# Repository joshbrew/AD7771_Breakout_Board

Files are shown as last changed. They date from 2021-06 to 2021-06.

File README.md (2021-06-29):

# AD7771_Breakout_Board
Unfinished AD7771 Breakout design. It works it's just not final.

The flex pieces were just unfinished thought experiments on a quick and dirty way to implement these AD7771 boards for FNIRS.

The board designs do work, but the Isolated DC-DC converter pin declarations in the schematics are backwards, found out the hard way so it is fixed in the design just not the footprint names in the .sch

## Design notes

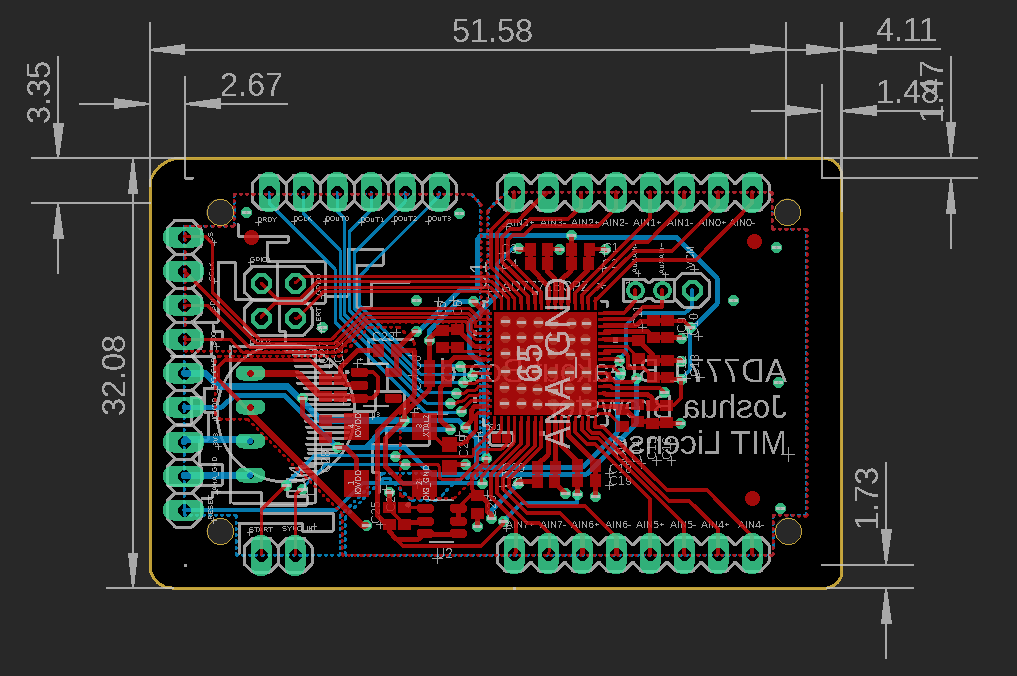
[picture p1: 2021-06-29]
AD7771.PNG

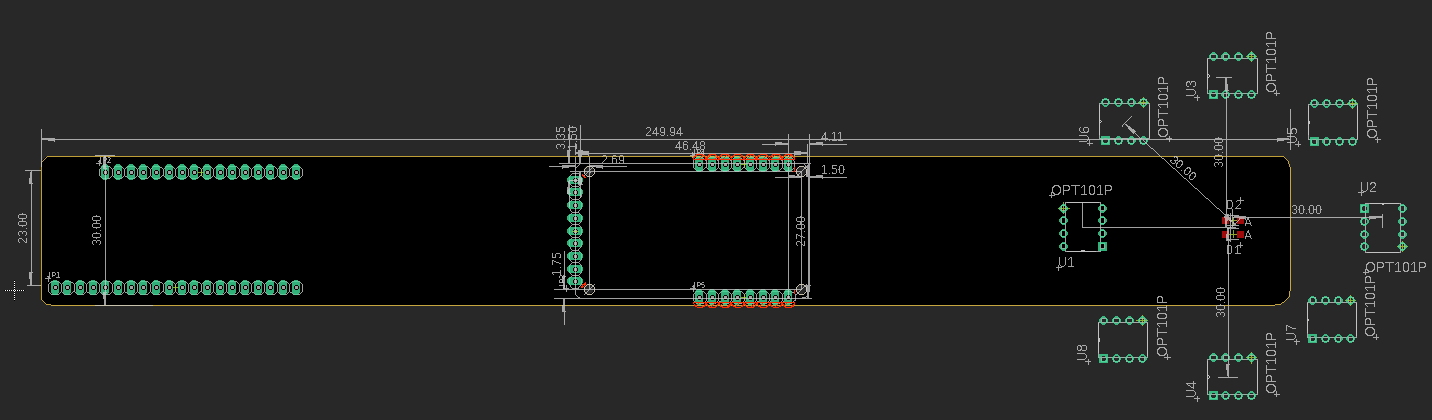
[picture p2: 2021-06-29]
FlexPiece_OCTO_Unfinished.PNG

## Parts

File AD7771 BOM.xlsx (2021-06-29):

Designation | Qty | Package | Value | Part # | Mouser Prices (high) | 1 | 10 | 100 | 1000 | Link
U1 | 1 |  |  | AD7771BCPZ | 584-AD7771BCPZ | 18.23 | 167.5 | 1345 | 11360 | https://www.mouser.com/ProductDetail/Analog-Devices/AD7771BCPZ
U2 | 1 |  |  | MAX6070AAUT25T | 700-MAX6070AAUT25+T | 2.63 | 23.6 | 183 | 1600 | https://www.mouser.com/ProductDetail/Maxim-Integrated/MAX6070AAUT25%2bT
U3 | 1 |  |  | LP5907MFX-3.3/NOPB | 595-LP5907MFX-3.3NPB | 0.55 | 4.31 | 32 | 191 | https://www.mouser.com/ProductDetail/Texas-Instruments/LP5907MFX-33-NOPB
U4 | 1 |  |  | TBA 1-0310 | 495-TBA1-0310 | 3.24 | 31.7 | 280 | 2430 | https://www.mouser.com/ProductDetail/TRACO-Power/TBA-1-0310
U5 | 1 |  |  | SG-210STF8.1920ML3 | 732-SG210STF8.1920L3 | 1.18 | 10.9 | 93.3 | 764 | https://www.mouser.com/ProductDetail/Epson-Timing/SG-210STF-81920ML3
C1, C3, C5, C8, C10, C13, C16, C19, C21, C22, C23 | 11 | C0402 | 1uF |  | 963-JMK105BJ105KP-F | 1.1 | 4.95 | 35.2 | 275 | https://www.mouser.com/ProductDetail/Taiyo-Yuden/JMK105BJ105KP-F?qs=vF%252B8ahGVilcfgxT2k6hjqQ%3D%3D
C2, C4, C6, C7, C9, C11, C12, C14, C15, C17, C18, C20, C24, C25, C26 | 14 | C0402 | 100nF |  | 963-LMF105B7104KVHF | 1.4 | 4.2 | 28 | 182 | https://www.mouser.com/ProductDetail/Taiyo-Yuden/LMF105B7104KVHF
C27 | 1 | C0402 | 10uF |  | 963-JMK105CBJ106MV-F | 0.22 | 1.02 | 8 | 51
 |  |  |  | via PCBway: | PCB Estimate (lead-free) | 18 | 18 | 50 | 235 | HASL lead free, 27mmX46.5mm, 2mm thick, any finish
 |  |  |  |  | Assembly Estimate | 88 | 88 | 232 | 520
 |  |  |  |  | Totals | 134.55 | 354.18 | 2286.5 | 17608
 |  |  |  | Additional Flex Piece Parts
 |  |  |  | OPT 101 |  | 0.9 | 9 | 90 | 900 | Aliexpress estimate
 |  |  |  | BR1102W |  | 0.5 | 3.09 | 14.2 | 119 | https://www.mouser.com/ProductDetail/Stanley-Electric/BR1102W-TR
 |  |  |  | HAN1102W |  | 0.38 | 2.5 | 16.1 | 126 | https://www.mouser.com/ProductDetail/Stanley-Electric/HAN1102W-1-TR
 |  |  |  | LOLIN32 |  | 4 | 40 | 400 | 4000 | Aliexpress estimate
 |  |  |  |  | Flex board by PCBway | 131 | 152 | 375 | 2336 | 250mmX30mm, 0.23mm thickness, 0.7mm thick FR4 stiffener (boths sides for manual assembly), ENIG
 |  |  |  |  | Extended Totals | 271.33 | 560.77 | 3181.8 | 25089
 |  |  |  | Other
 |  |  |  | Batteries | 300mAh-500mAh
 |  |  |  | Headband | Neoprene + plastic casing, something for the flex part.
 |  |  |  | Labor | Assembling the whole thing, testing, and packaging (done in-house)

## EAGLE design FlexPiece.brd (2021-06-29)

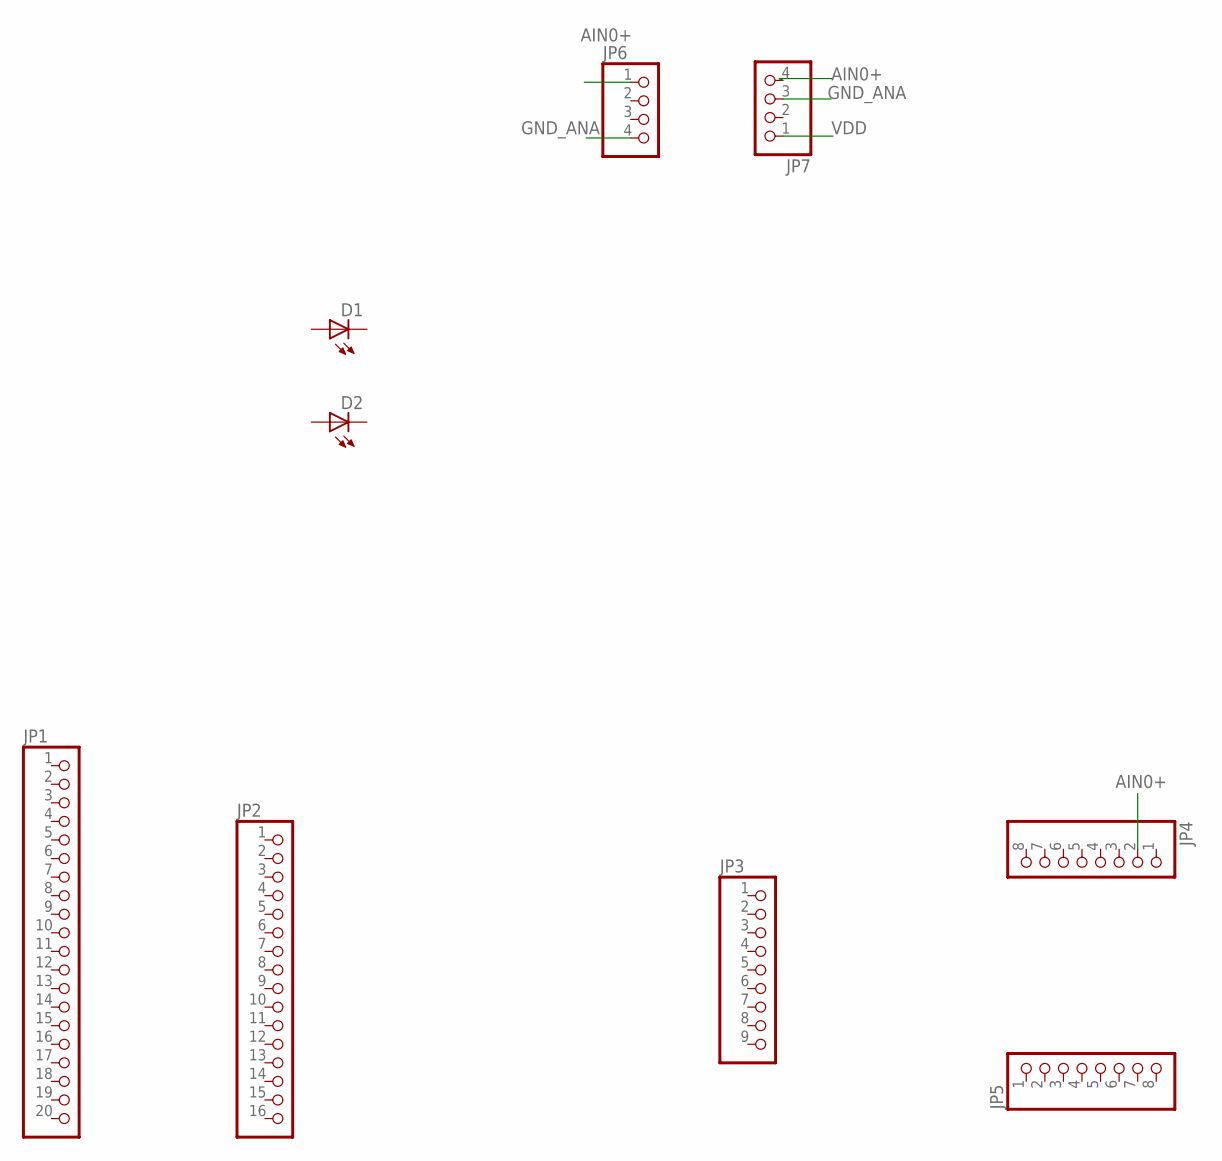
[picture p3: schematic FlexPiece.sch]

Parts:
D1, D2: LED1206; LED-1206
JP1: PINHD-1X20; 1X20
JP2: PINHD-1X16; 1X16
JP3: PINHD-1X9; 1X09
JP4, JP5: PINHD-1X8; 1X08
JP6, JP7: PINHD-1X4; 1X04

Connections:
AIN0+: JP4.2, JP6.1, JP7.4
GND_ANA: JP6.4, JP7.3
VDD: JP7.1

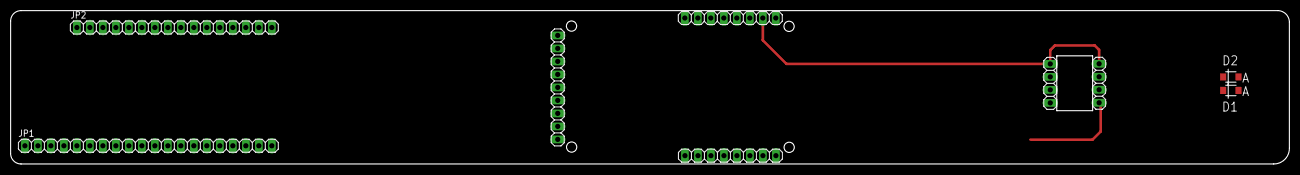
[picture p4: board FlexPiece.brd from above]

Board: 2 copper layers, 249.9 x 30.0 mm, 9 parts (0 on the bottom side), 2 nets.

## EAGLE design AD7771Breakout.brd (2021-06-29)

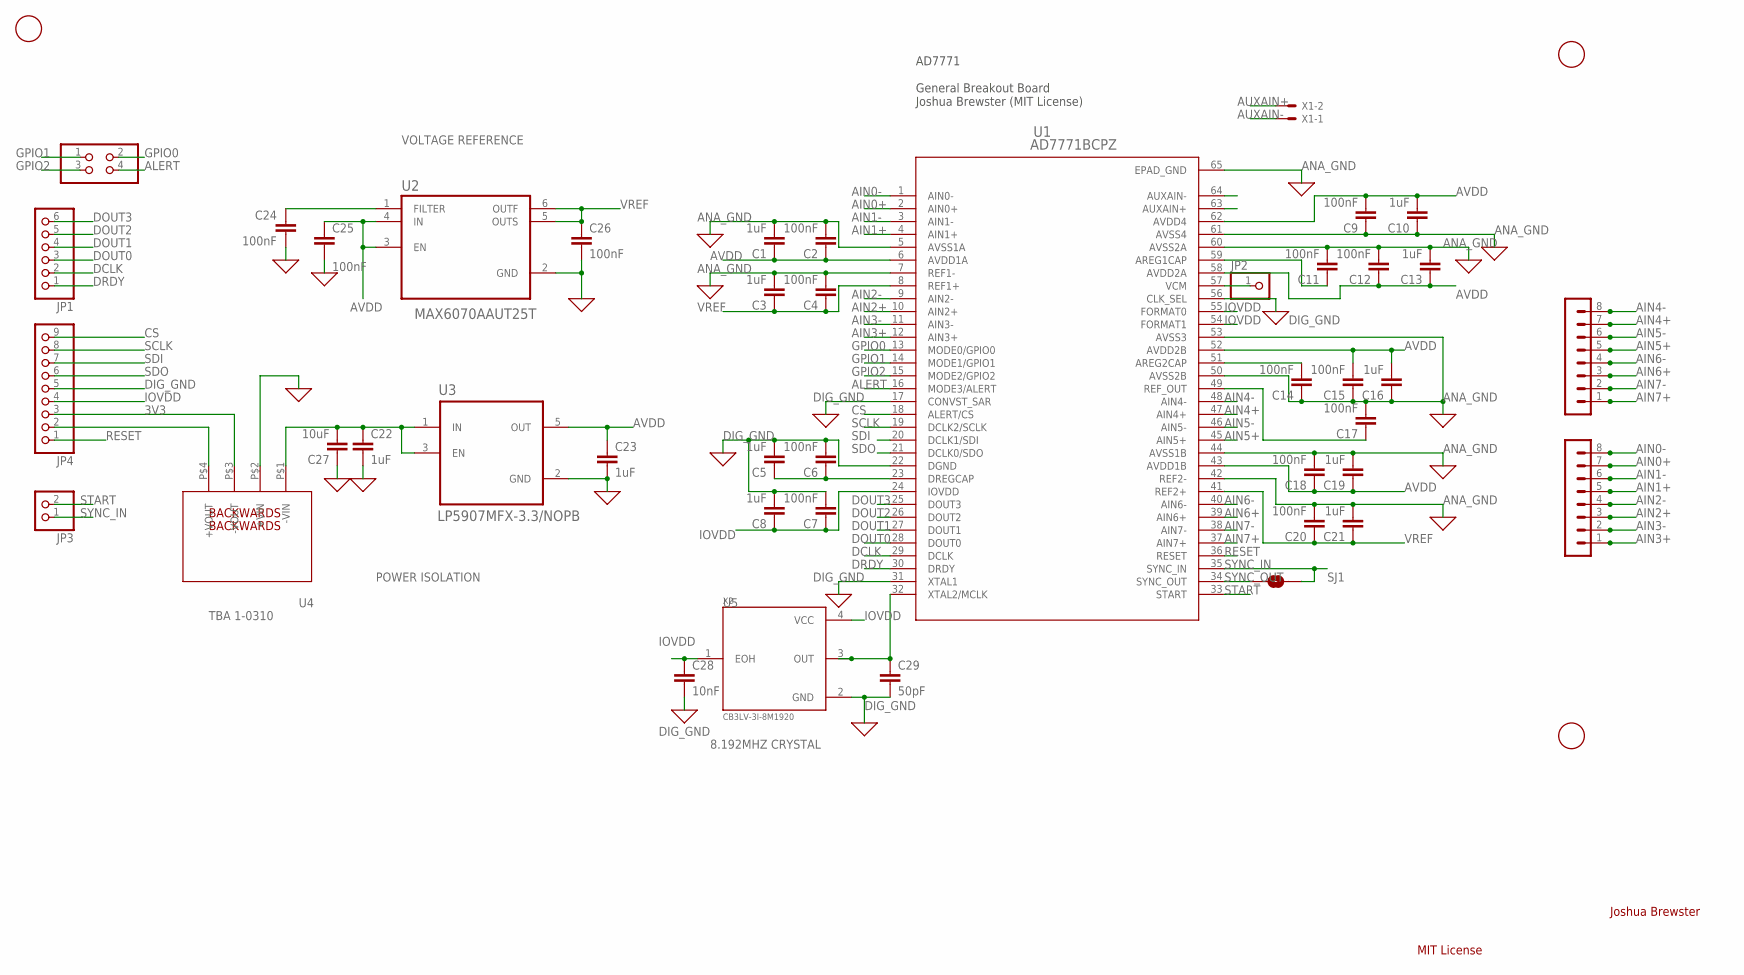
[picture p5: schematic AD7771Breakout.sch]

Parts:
C1, C3, C5, C8, C10, C13, C16, C19, C21, C22, C23: 1uF; C0402
C2, C4, C6, C7, C9, C11, C12, C14, C15, C17, C18, C20, C24, C25, C26: 100nF; C0402
C27: 10uF; C0402
C28: 10nF; C0402
C29: 50pF; C0603
JP1: PINHD-1X6; 1X06
JP2: PINHD-1X1; 1X01
JP3: PINHD-1X2; 1X02
JP4: PINHD-1X9; 1X09
JP5: PINHD-2X2; 2X02
SJ1: SOLDERJUMPERNC; SJ_2S_SMALL
SV4, SV5: MA08-1
U1: AD7771BCPZ; CP_64_15_ADI
U2: MAX6070AAUT25T; SOT95P280X145-6N
U3: LP5907MFX-3.3/NOPB; SOT95P280X145-5N
U4: TBA1-0310; SIP4-KT
U$1, U$2, U$5: FIDUCIAL; FIDUCIAL_1MM
X1: 332-02
X2: CB3LV-3I-8M1920; OSCCC700X500X180-4N

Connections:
3V3: JP4.3, U4.P$3 (-VOUT)
AGND_OUT: JP4.2, U4.P$4 (+VOUT)
AIN0+: SV4.7, U1.2 (AIN0+)
AIN0-: SV4.8, U1.1 (AIN0-)
AIN1+: SV4.5, U1.4 (AIN1+)
AIN1-: SV4.6, U1.3 (AIN1-)
AIN2+: SV4.3, U1.10 (AIN2+)
AIN2-: SV4.4, U1.9 (AIN2-)
AIN3+: SV4.1, U1.12 (AIN3+)
AIN3-: SV4.2, U1.11 (AIN3-)
AIN4+: SV5.7, U1.47 (AIN4+)
AIN4-: SV5.8, U1.48 (AIN4-)
AIN5+: SV5.5, U1.45 (AIN5+)
AIN5-: SV5.6, U1.46 (AIN5-)
AIN6+: SV5.3, U1.39 (AIN6+)
AIN6-: SV5.4, U1.40 (AIN6-)
AIN7+: SV5.1, U1.37 (AIN7+)
AIN7-: SV5.2, U1.38 (AIN7-)
ALERT: JP5.4, U1.16 (MODE3/ALERT)
ANA_GND: C1.2, C2.2, C3.2, C4.2, C9.1, C10.1, C11.2, C12.2, C13.2, C14.1, C15.1, C16.1, C17.2, C18.2, C19.2, C20.2, C21.2, C22.2, C23.2, C24.2, C25.2, C26.2, C27.1, U1.5 (AVSS1A), U1.7 (REF1-), U1.42 (REF2-), U1.44 (AVSS1B), U1.50 (AVSS2B), U1.53 (AVSS3), U1.60 (AVSS2A), U1.61 (AVSS4), U1.65 (EPAD_GND), U2.2 (GND), U3.2 (GND), U4.P$2 (+VIN)
AREG1CAP: C11.1, U1.59 (AREG1CAP)
AREG2CAP: C14.2, U1.51 (AREG2CAP)
AUXAIN+: U1.63 (AUXAIN+), X1.2
AUXAIN-: U1.64 (AUXAIN-), X1.1
AVDD: C1.1, C2.1, C9.2, C10.2, C12.1, C13.1, C15.2, C16.2, C18.1, C19.1, C23.1, C25.1, U1.6 (AVDD1A), U1.43 (AVDD1B), U1.52 (AVDD2B), U1.58 (AVDD2A), U1.62 (AVDD4), U2.3 (EN), U2.4 (IN), U3.5 (OUT)
CS: JP4.9, U1.18 (ALERT/CS)
DCLK: JP1.2, U1.29 (DCLK)
DIG_GND: C5.2, C6.2, C7.2, C8.2, C28.2, C29.2, JP4.5, U1.17 (CONVST_SAR), U1.22 (DGND), U1.31 (XTAL1), U1.56 (CLK_SEL), X2.2 (GND)
DOUT0: JP1.3, U1.28 (DOUT0)
DOUT1: JP1.4, U1.27 (DOUT1)
DOUT2: JP1.5, U1.26 (DOUT2)
DOUT3: JP1.6, U1.25 (DOUT3)
DRDY: JP1.1, U1.30 (DRDY)
DREGCAP: C5.1, C6.1, U1.23 (DREGCAP)
FILTER: C24.1, U2.1 (FILTER)
GPIO0: JP5.2, U1.13 (MODE0/GPIO0)
GPIO1: JP5.1, U1.14 (MODE1/GPIO1)
GPIO2: JP5.3, U1.15 (MODE2/GPIO2)
IOVDD: C7.1, C8.1, C28.1, JP4.4, U1.24 (IOVDD), U1.54 (FORMAT1), U1.55 (FORMAT0), X2.1 (EOH), X2.4 (VCC)
REF_OUT: C17.1, U1.49 (REF_OUT)
RESET: JP4.1, U1.36 (RESET)
SCLK: JP4.8, U1.19 (DCLK2/SCLK)
SDI: JP4.7, U1.20 (DCLK1/SDI)
SDO: JP4.6, U1.21 (DCLK0/SDO)
START: JP3.2, U1.33 (START)
SYNC_IN: JP3.1, SJ1.2, U1.35 (SYNC_IN)
SYNC_OUT: SJ1.1, U1.34 (SYNC_OUT)
VCM: JP2.1, U1.57 (VCM)
VOUT+: C22.1, C27.2, U3.1 (IN), U3.3 (EN), U4.P$1 (-VIN)
VREF: C3.1, C4.1, C20.1, C21.1, C26.1, U1.8 (REF1+), U1.41 (REF2+), U2.5 (OUTS), U2.6 (OUTF)
XTAL2: C29.1, U1.32 (XTAL2/MCLK), X2.3 (OUT)

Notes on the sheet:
AD7771 General Breakout Board Joshua Brewster (MIT License)
TBA 1-0310
POWER ISOLATION
VOLTAGE REFERENCE
8.192MHZ CRYSTAL
Joshua Brewster
MIT License
BACKWARDS

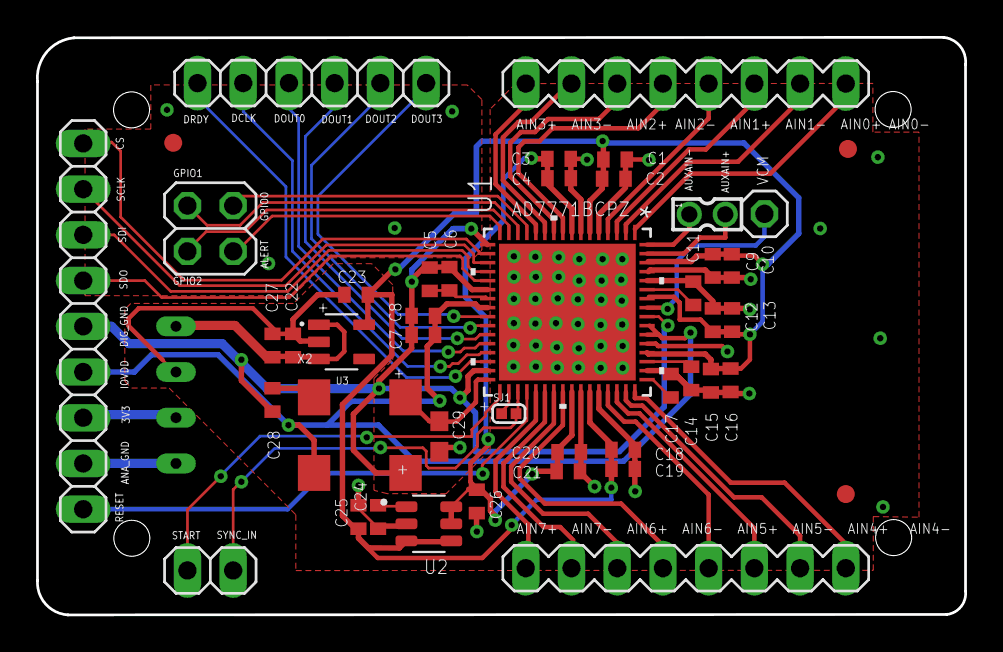
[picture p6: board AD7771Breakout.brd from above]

Board: 2 copper layers, 51.6 x 32.1 mm, 46 parts (1 on the bottom side), 51 nets.
